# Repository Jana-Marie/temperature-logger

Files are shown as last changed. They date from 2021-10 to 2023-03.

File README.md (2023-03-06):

# temperature-logger

Anotter USB temperature logger that can record up to four channels with thermocouple or NTCs connected via CDC directly or SCPI to USB. You can choose how you want to receive the data by moving the selector switch next to the Type-C receptacle. If you switch to CSV, it will simply output all connected channels to your console in a machine and human readable format (CSV or TSV, I prefer TSV) at about 10 readings per second. If you switch to SCPI, an SCPI terminal is displayed via USB so that you can integrate the logger into your lab equipment. This is particularly handy because you can also use it to control the OC- or H-Bridge outputs, which turns the logger into a thermal IO card. This can be useful when working with Peltier- and heating elements.

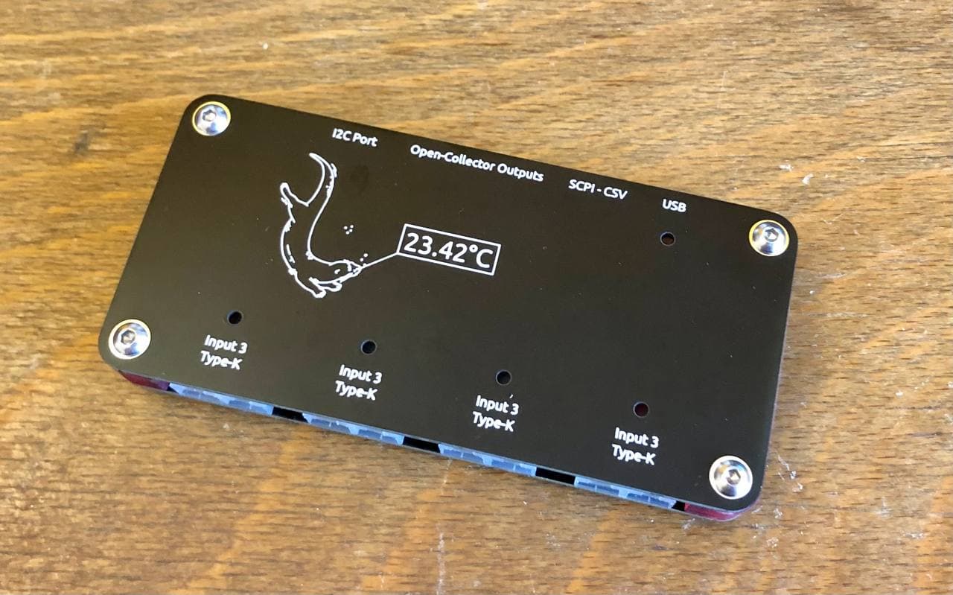
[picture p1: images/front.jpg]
front


Having needed a temperature logger several times in the past, after hacking two together for spontaneous testing, I decided to develop a proper one. This is my result. :3

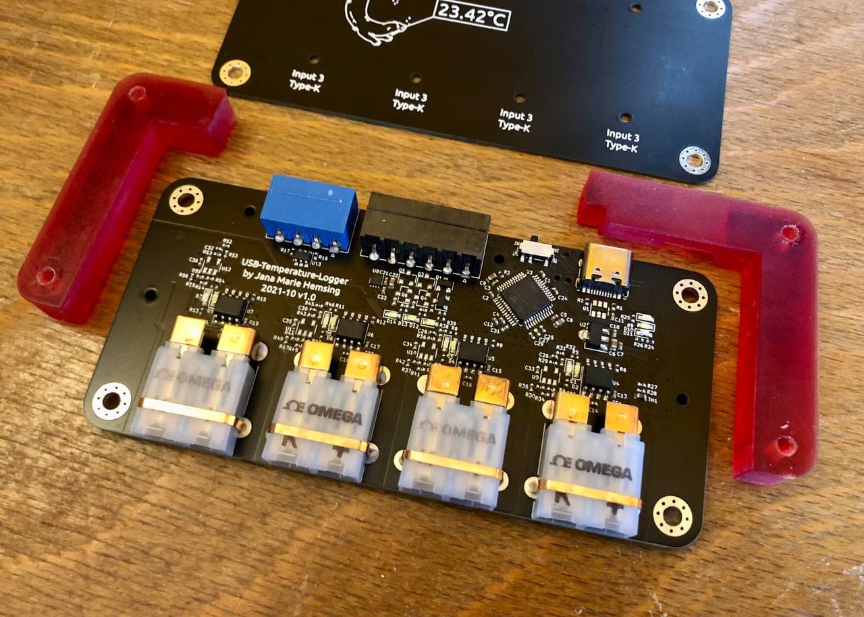
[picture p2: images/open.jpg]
open


### Inputs

Each of the four inputs can either be configured as thermocouple or NTC (resistance measuring) input. At the moment they are assembly options, I need to test if I can assmble both at the same time.

**thermocouple**

One MAX31855KASA can be populated per channel, enabling the reading of K-type thermocouples. Other versions of this IC are available if other thermocouple types are required.

**NTC**

The NTC amplifier is based on [this appnote](https://www.ti.com/lit/an/sboa323a/sboa323a.pdf) and allows amplification of small ranges to the full ADC range. This was an important motivation for this project as I needed a multi-channel body temperature logger.

If you want to know more, you can check out the [schematic](https://github.com/Jana-Marie/temperature-logger/blob/main/temperature-logger.pdf).

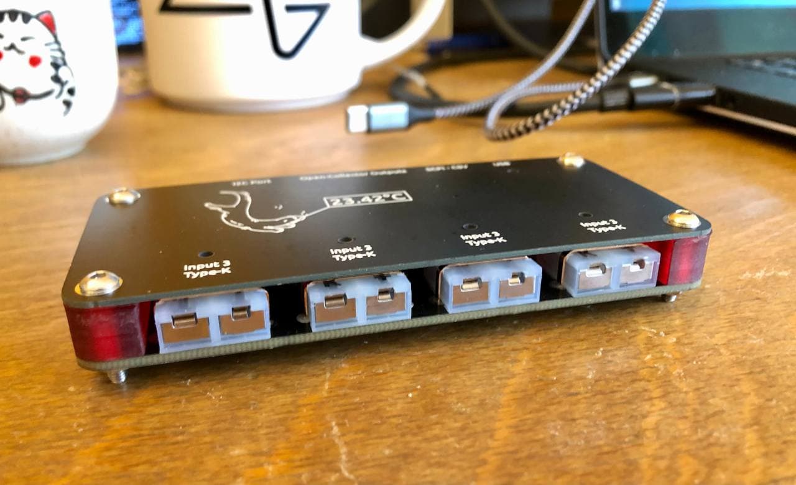
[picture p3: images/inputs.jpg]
inputs


### TODO

 - [ ] implement SCPI - done in the SCPI branch, check it out, but there is not much space left on the STM32, hence no merge yet
 - [ ] add sigrok communication/protocol 

### License

Copyright Jana Marie Hemsing 2023.

This source describes Open Hardware and is licensed under the CERN-OHL-S v2.

You may redistribute and modify this source and make products using it under
the terms of the CERN-OHL-S v2 (https://ohwr.org/cern_ohl_s_v2.txt).

This source is distributed WITHOUT ANY EXPRESS OR IMPLIED WARRANTY,
INCLUDING OF MERCHANTABILITY, SATISFACTORY QUALITY AND FITNESS FOR A
PARTICULAR PURPOSE. Please see the CERN-OHL-S v2 for applicable conditions.

Source location: https://github.com/Jana-Marie/temperature-logger

As per CERN-OHL-S v2 section 4, should You produce hardware based on this
source, You must where practicable maintain the Source Location visible
on the external case of the Gizmo or other products you make using this
source.

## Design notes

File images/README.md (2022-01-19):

front
open
inputs
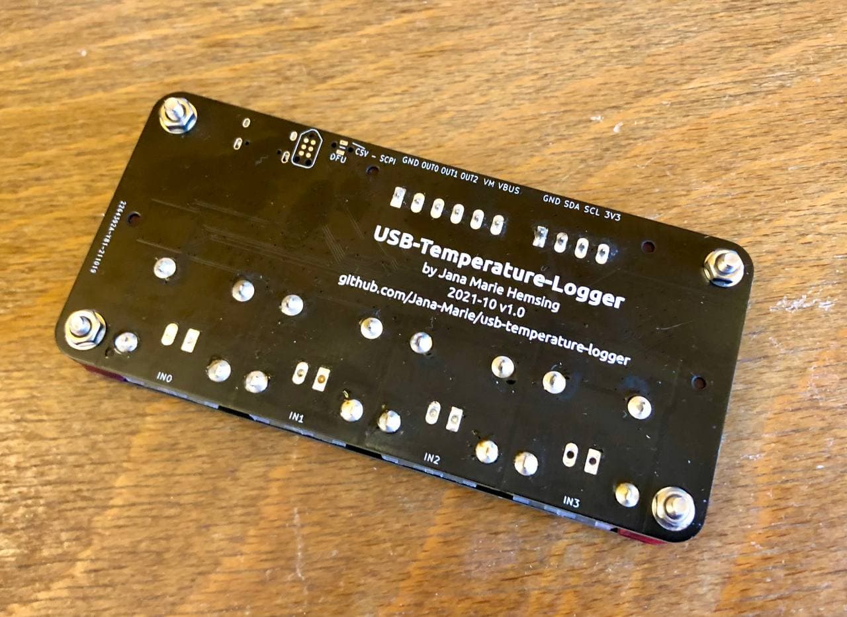
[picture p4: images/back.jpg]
back

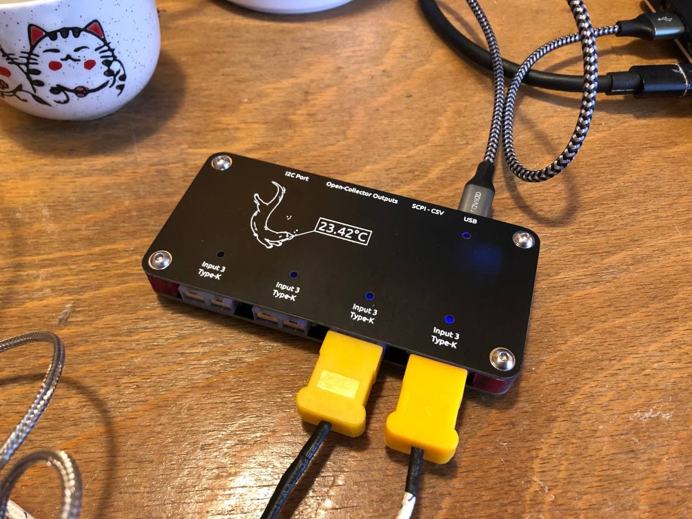
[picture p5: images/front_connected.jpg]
front_connected

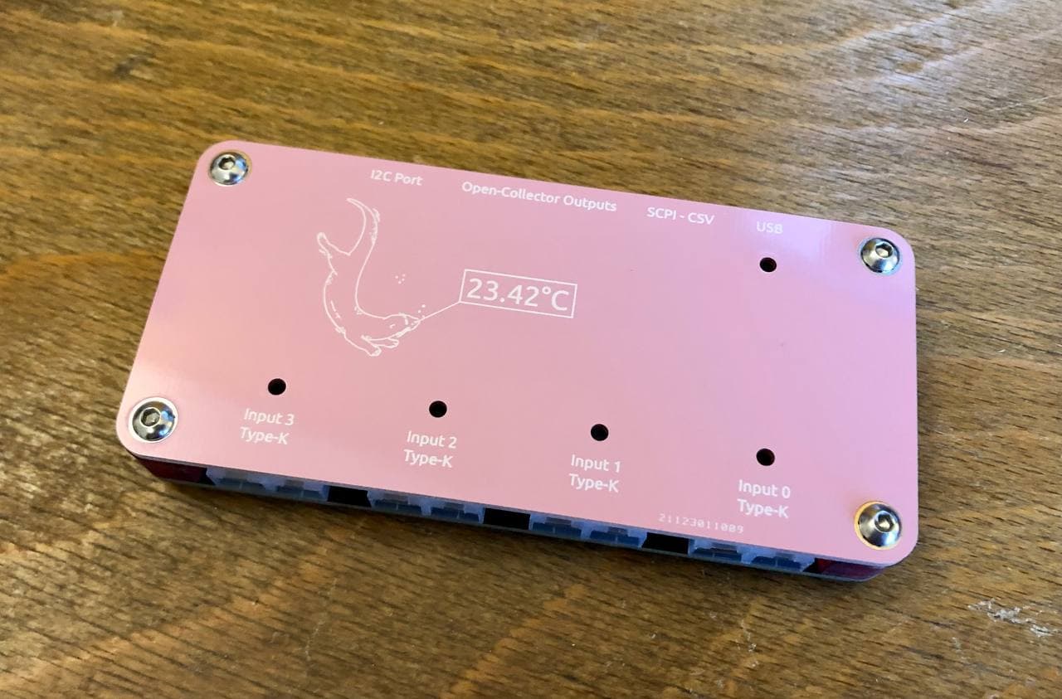
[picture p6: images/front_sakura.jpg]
front_sakura


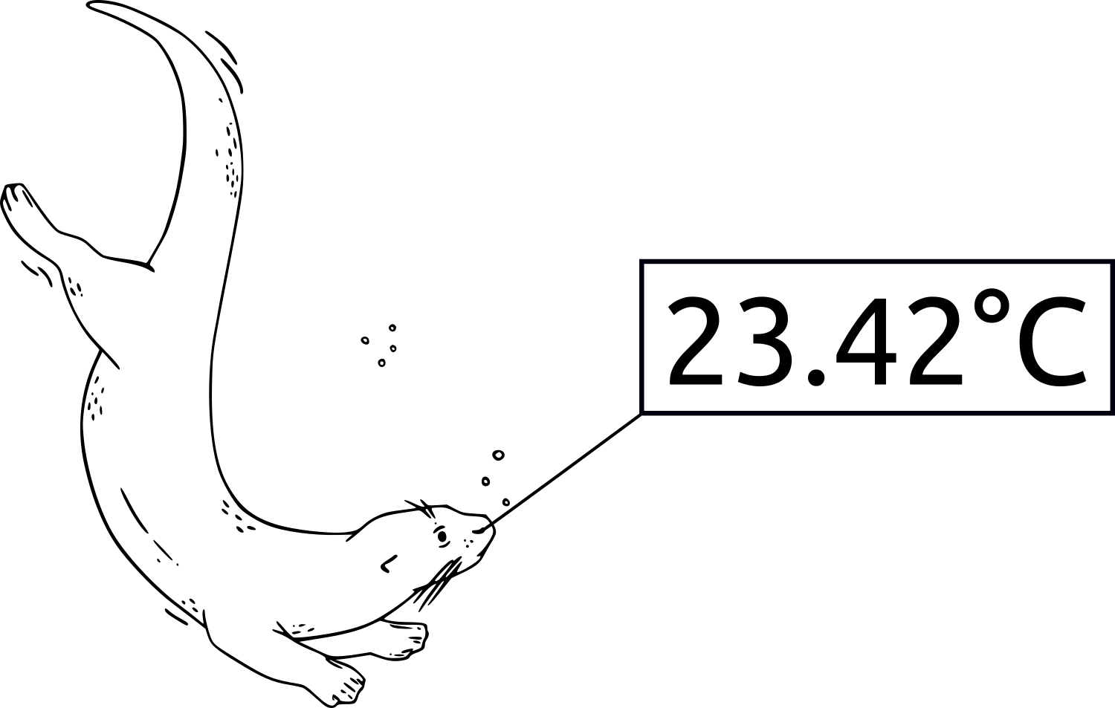
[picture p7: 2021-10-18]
blind_tc/outfiles/text3608.png

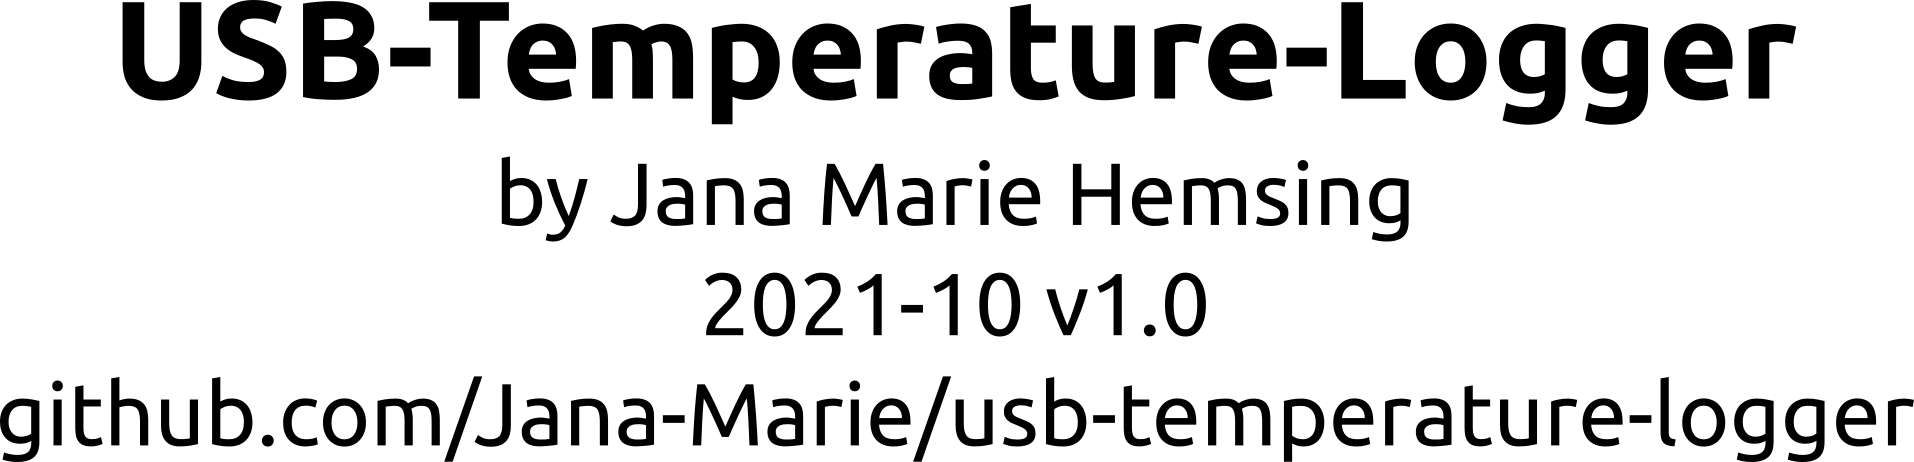
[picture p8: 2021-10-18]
outfiles/text856-3.png

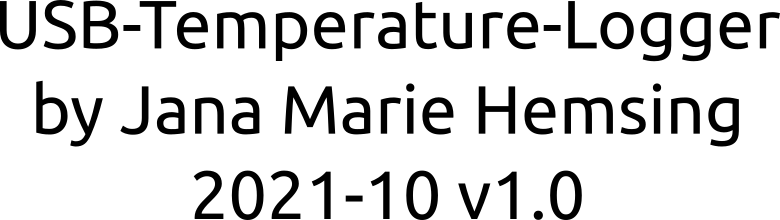
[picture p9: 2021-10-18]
outfiles/text856.png

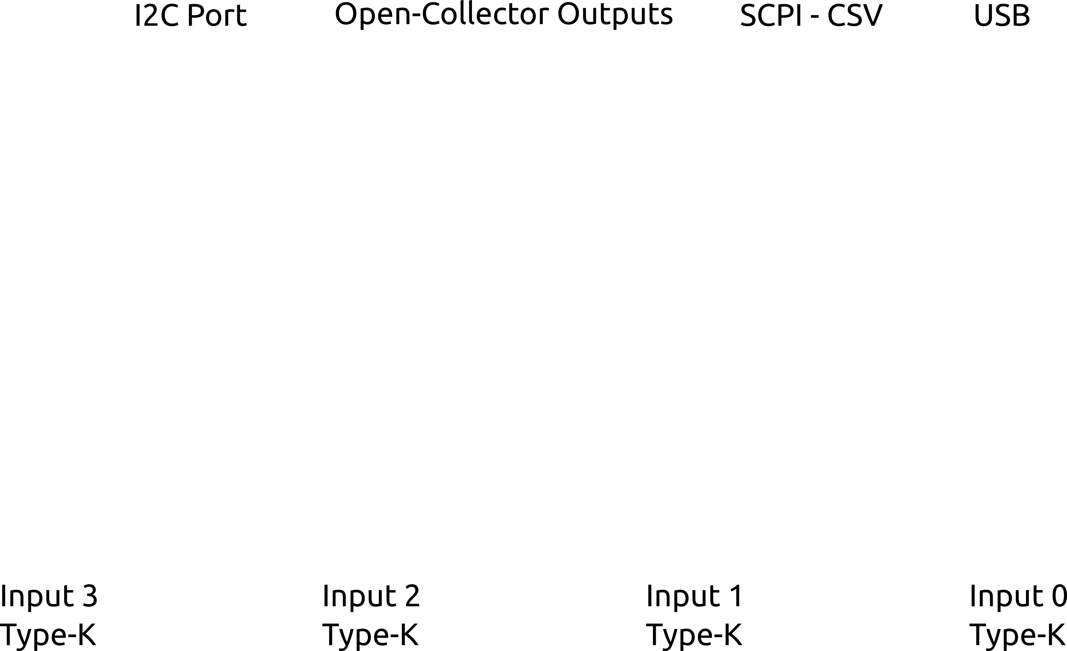
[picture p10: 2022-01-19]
blind_tc/outfiles/text2807.png

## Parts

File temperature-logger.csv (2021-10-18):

Comment | Designator | Footprint | LCSC
100n | C12,C7,C10,C11,C1,C2,C3,C4,C5,C24,C13,C15,C17,C19 | otter:C_0402
10n | C14,C26,C16,C28,C18,C30,C20,C32 | otter:C_0402
DNP | C22 | otter:C_0603
DNP | C25,C33,C27,C34,C29,C35,C31,C36,C23,C21 | otter:C_0402
1uF | C8,C9,C6 | otter:C_0603
GREEN | D10,D2,D4,D6,D8,D14,D13,D12 | otter:LED_0603_1608Metric
BLUE | D11 | otter:LED_0603_1608Metric
RED | D9,D1,D3,D5,D7 | otter:LED_0603_1608Metric
FERRET | FB2,FB1,FB4,FB3,FB6,FB5,FB8,FB7 | otter:L_0402
M3 | H1,H2,H3,H4 | MountingHole:MountingHole_3.2mm_M3_Pad_Via
USB | J1 | otter:USB-C 16Pin
THERMOCOUPLE | J2,J3,J4,J5 | otter:PCC-SMP
OUT | J6 | Connector_Phoenix_MC:PhoenixContact_MC_1,5_6-G-3.5_1x06_P3.50mm_Horizontal
I2C | J7 | Connector_Phoenix_MC:PhoenixContact_MC_1,5_4-G-3.5_1x04_P3.50mm_Horizontal
DNP | J8,J9,J10,J11 | otter:PhoenixContact_MC_1,5_2-G-3.5_1x02_P3.50mm_Horizontal
DFU | JP1 | otter:R_0805
TC2030 | P1 | otter:TC2030
2N7002 | Q1,Q3,Q5 | Package_TO_SOT_SMD:SOT-23
BC817 | Q2,Q4,Q6 | Package_TO_SOT_SMD:SOT-23
5k1 | R1,R2,R3,R27,R28,R16,R17 | otter:R_0402
220 | R24,R25,R26,R4,R5,R7,R8,R10,R11,R13,R14,R19,R18,R21,R20,R23,R22,R59,R58,R57 | otter:R_0402
DNP | R35,R33,R29,R32,R31,R34,R30,R42,R40,R36,R39,R38,R41,R37,R49,R47,R43,R46,R45,R48,R44,R56,R54,R50,R53,R52,R55,R51 | otter:R_0402
10 | R6,R9,R12,R15 | otter:R_0402
SCPI_CSV | SW1 | Button_Switch_SMD:SW_SPDT_PCM12
NTC | TH1 | otter:R_0603
USBLC6-4 | U1,U13 | Package_TO_SOT_SMD:SOT-23-6
AP2204R-3.3 | U2 | Package_TO_SOT_SMD:SOT-89-3
STM32F072C8Tx | U3 | Package_QFP:LQFP-48_7x7mm_P0.5mm
MAX31855KASA | U4,U5,U6,U7 | Package_SO:SOIC-8_3.9x4.9mm_P1.27mm
DRV8837 | U8 | Package_SON:WSON-8-1EP_2x2mm_P0.5mm_EP0.9x1.6mm
TLV9001 | U9,U10,U11,U12 | Package_TO_SOT_SMD:SOT-23-5

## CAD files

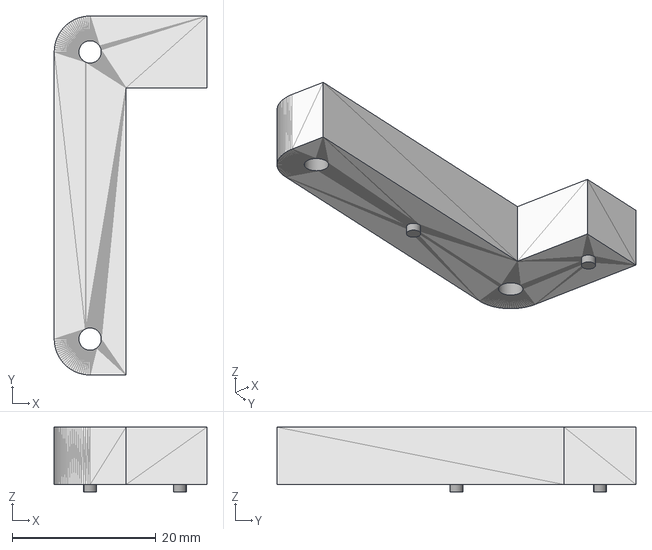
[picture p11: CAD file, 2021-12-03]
3D/spacer_left.step
21.2 x 50.0 x 9.00 mm

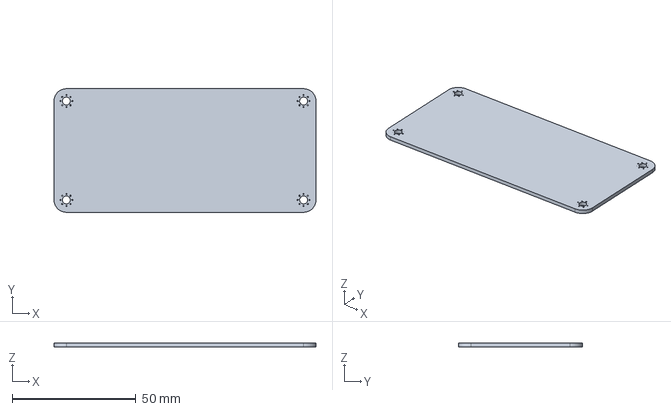
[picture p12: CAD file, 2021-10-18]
blind_tc/blind_tc.step
106.0 x 50.0 x 1.60 mm

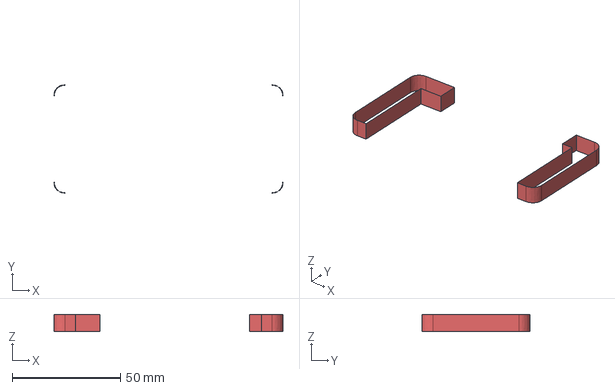
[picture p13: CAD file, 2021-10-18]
outfiles/part.step
106.0 x 50.0 x 8.00 mm

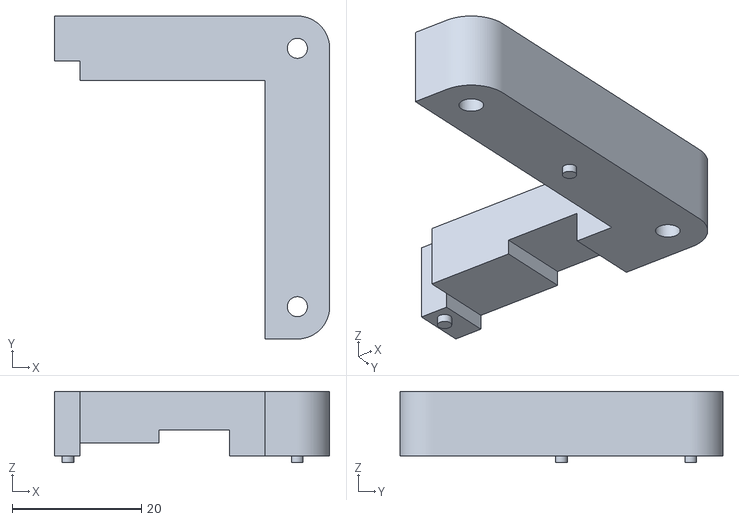
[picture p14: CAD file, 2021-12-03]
3D/sapcer_right.stl
42.6 x 50.0 x 11.0

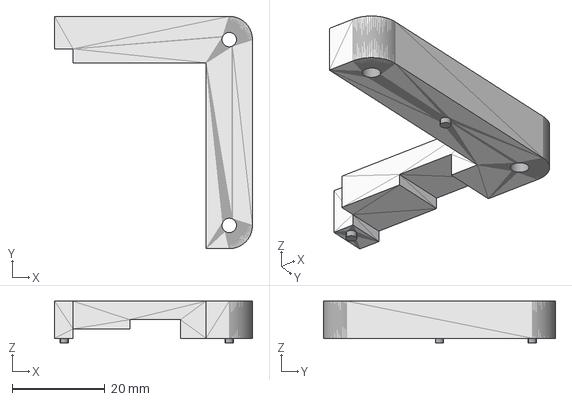
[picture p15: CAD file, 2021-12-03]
3D/spacer_right.step
42.6 x 50.0 x 9.00 mm

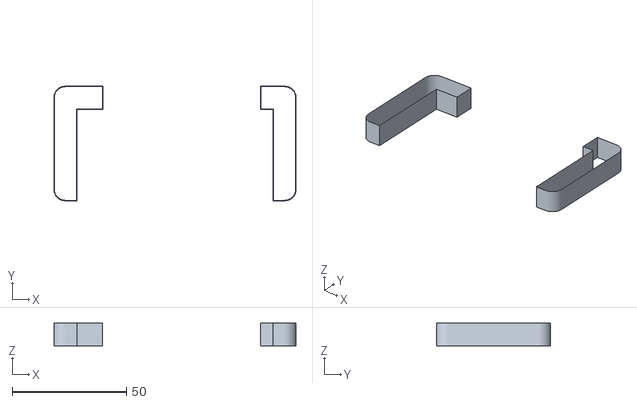
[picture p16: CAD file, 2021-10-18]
outfiles/spacer.stl
106.0 x 50.0 x 10.0

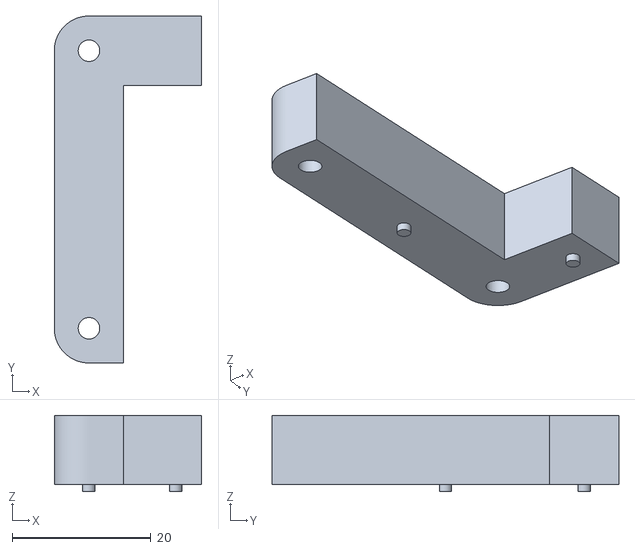
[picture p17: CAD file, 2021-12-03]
3D/sapcer_left.stl
21.2 x 50.0 x 11.0

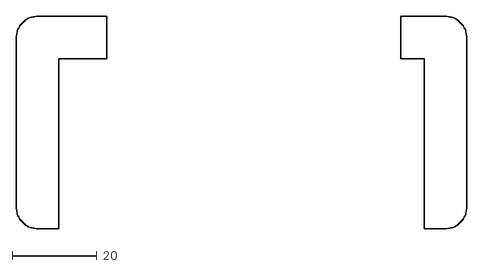
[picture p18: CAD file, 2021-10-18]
outfiles/temperature-logger-brd.dxf
106.0 x 50.0

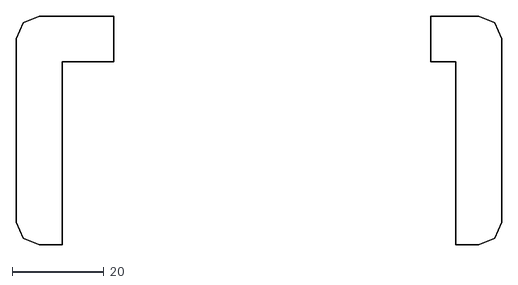
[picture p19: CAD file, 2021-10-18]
outfiles/parts.dxf
106.0 x 50.0

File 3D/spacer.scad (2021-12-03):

$fn = 100;

right();
//left();

module left(z=10){
    difference(){
        union(){
            translate([0,0,z/2])cube([10,40,z],center=true);
            translate([0,20,0])cylinder(r=5,h=z);
            translate([0,-20,0])cylinder(r=5,h=z);
            translate([16.25/2,20,z/2])cube([16.25,10,z],center=true);
            translate([2.5,-20-2.5,z/2])cube([5,5,z],center=true);
            
            translate([0,0,-1])cylinder(r=.9,h=1);
            translate([12.5,20,-1])cylinder(r=.9,h=1);
        } union(){
            translate([0,-20,-0.1])cylinder(d=3.1,h=z+0.2);
            translate([0,20,-0.1])cylinder(d=3.1,h=z+0.2);
        }
    }
}

module right(z=10){
    difference(){
        union(){
            translate([0,0,z/2])cube([10,40,z],center=true);
            translate([-2.5,-20-2.5,z/2])cube([5,5,z],center=true);
            translate([0,20,0])cylinder(r=5,h=z);
            translate([0,-20,0])cylinder(r=5,h=z);
            translate([-10.5/2,20,z/2])cube([10.5,10,z],center=true);
            translate([-10.925/2-10.5,20,z-(z-4)/2])cube([10.925,10,z-4],center=true);
            translate([-12.2/2-10.5-10.925,20,z-(z-2)/2])cube([12.2,10,z-2],center=true);
            translate([-4/2-10.5-10.925-12.2,20+1.5,z/2])cube([4,7,z],center=true);
            
            
            translate([0,0,-1])cylinder(r=.9,h=1);
            translate([-35.5,20,-1])cylinder(r=.9,h=1);
        } union(){
            translate([0,-20,-0.1])cylinder(d=3.1,h=z+0.2);
            translate([0,20,-0.1])cylinder(d=3.1,h=z+0.2);
        }
    }
}

module right_simple(z=8){
    difference(){
        union(){
            translate([0,0,z/2])cube([10,40,z],center=true);
            translate([0,20,0])cylinder(r=5,h=z);
            translate([0,-20,0])cylinder(r=5,h=z);
            translate([-10.5/2,20,z/2])cube([10.5,10,z],center=true);
            //translate([2.5,-20-2.5,z/2])cube([5,5,z],center=true);
            
            translate([0,0,-1])cylinder(r=.9,h=1);
            //translate([12.5,20,-1])cylinder(r=.9,h=1);
        } union(){
            translate([0,-20,-0.1])cylinder(d=3.1,h=z+0.2);
            translate([0,20,-0.1])cylinder(d=3.1,h=z+0.2);
        }
    }
}

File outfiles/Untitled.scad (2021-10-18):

linear_extrude(height = 10, center = true, convexity = 100)
   import (file = "temperature-logger-brd.dxf");

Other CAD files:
outfiles/extrude.step
outfiles/part.FCStd

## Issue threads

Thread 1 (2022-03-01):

### ISSUE TITLE
DRC failures: unconnected GND pin and different pin for NTC_BOARD net

### ISSUE THREAD

**Issue by festlv** [Jana-Marie/temperature-logger#1]
First of all, thanks for sharing this project. I have had a similar need of logging a couple of thermocouple channels, but so far, not enough of a need to design something like this myself.

When reviewing the board before ordering it I noticed a couple of DRC violations- most of them are harmless, but two did catch my attention:
1) Pin 35 of U3 (GND) is not connected- probably a later routing change made it an island.
2) Net NTC_BOARD is connected to pin 29 of U3 in PCB layout, but in schematic it's connected to pin 18.

I'd submit a PR for item #1, but I also squeezed the width of the board a bit to get below 100mm threshold, so that JLCPCB doesn't apply large board engineering fee.

**Comment by Jana-Marie** [comment]
oh, shit, why didn't I get a notification for this issue >.< Will get back to you as soon as possible! The NTC pin is a known issue, I somehow connected it to the wrong pin, fixed it in schematic to not forget it and never updated the board. I will do this as soon as possible!

**Comment by Jana-Marie** [comment]
Also, I would love to see a squeezed version of this board! :O

**Comment by Jana-Marie** [comment]
Please let me know, if you make a squeezed version! :)

**Comment by Jana-Marie** [comment]
omg, this is soo cool! Thank you for sharing it! :)

I think this is super helpful for others, I will order the squeezed version myself for sure. Threaded inserts are awesome, I like that idea. 

May I ask, what do you need/expect from the firmware? It is quite alpha at the moment, I would like to know which part of it would be for your advantage, so I can focus on that?

**Comment by festlv** [comment]
If you're interested, I can ship you my leftover PCBs and stencil, I won't need more boards in forseeable future. I can also print the enclosure and throw in the needed hardware. The only issue is that NTC_BOARD pin needs to be bodged to PB0 (for some reason I went with PA8, without checking that it's not routed to ADC).

Firmware wise I really don't need much- the only thing I noticed was that disconnected TC's are not reported, so the order of channels may change depending on how many channels are connected. For logging purposes I would prefer that channels are always reported in the same order, which would probably imply also reporting disconnected channels.

One thing which I will probably look into myself once I get around it: adding a support for I2C OLED (e.g. SSD1306 based modules) on the expansion port, just to be able to verify that the probes are connected correctly. On the other hand, I guess the LEDs for each channel are also there for this purpose (haha, I now have to check if I haven't soldered them backwards) :)

**Comment by Jana-Marie** [comment]
Okay, perfect, thank you for your input :3

I've pushed a small change, which will always send all channels and show the channel status via the onboard LEDs. Unconnected channels will deliver afaik a very high result, not sure what such a channel should show. Any string might be as annoying as a high number. A typical error-number (-1) would be a valid temperature, I could simply send an empty string there '', not sure if that has any drawbacks. Any suggestions from your side?

The ntc thing is probably my fault, I noticed it, but did not fix it in time. I am sorry for that.

I would be super interested in your boards actually. Do you have an email for me, or should I DM you via twitter?

**Comment by Jana-Marie** [comment]
Whops, had a bug in the FW, the leds do now show the state per channel

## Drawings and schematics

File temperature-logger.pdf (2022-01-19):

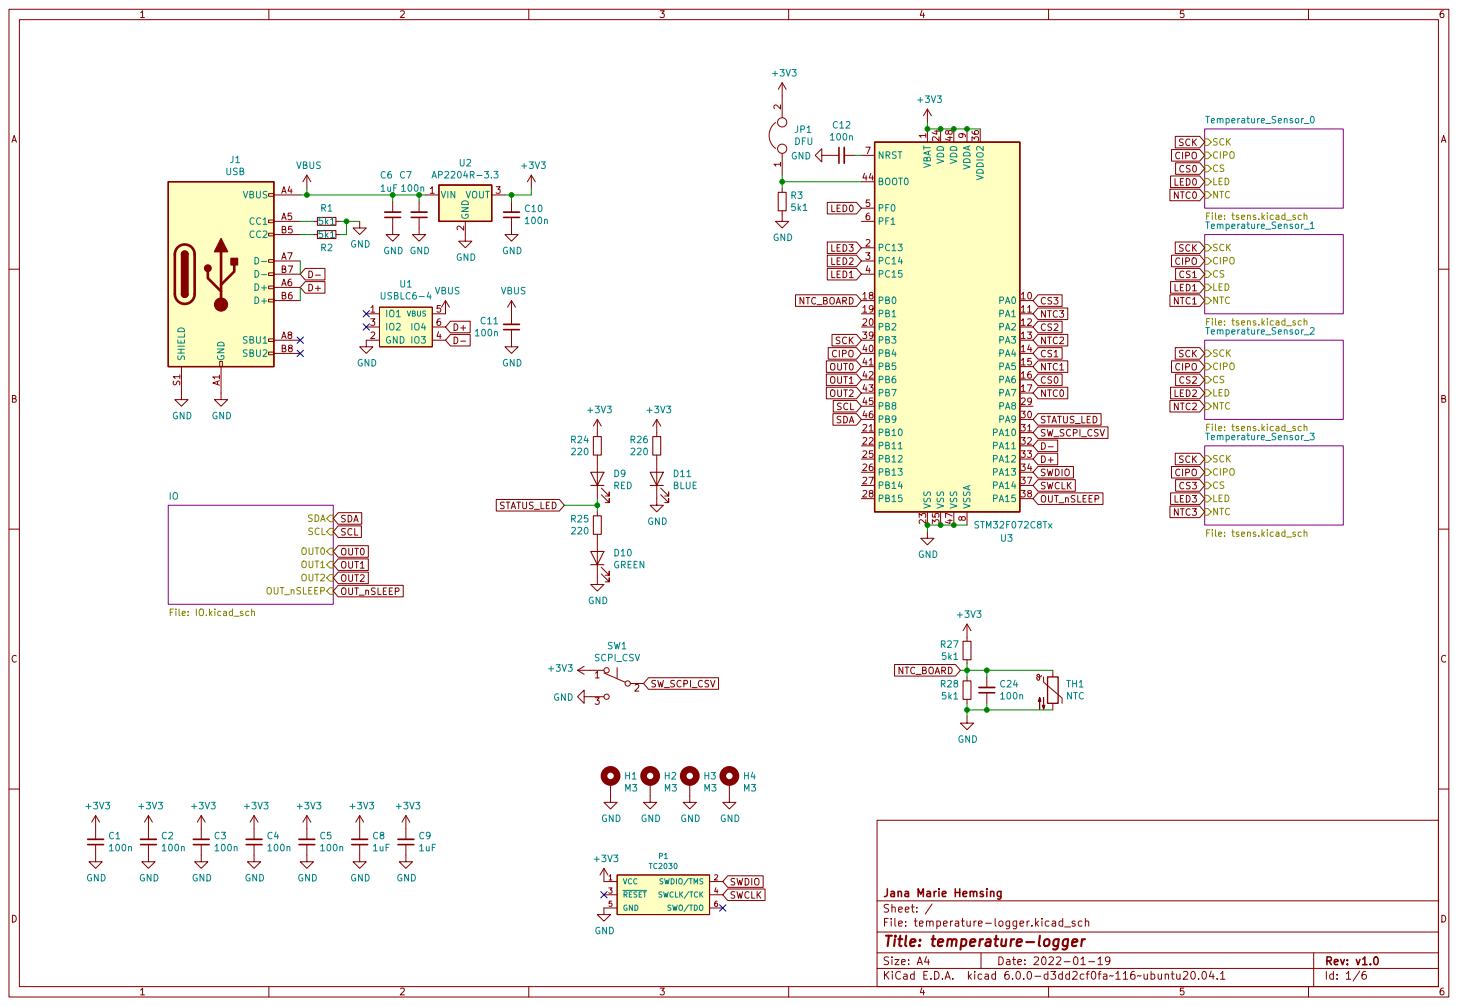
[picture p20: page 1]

1 PA0 10 PA1 11 PA2 12 PA3 13 PA4 14 PA5 15 PA6 16 PA7 17 PB0 18 PB1 19 PC13 2 PB2 20 PB10 21 PB11 22 VSS 23 VDD 24 PB12 25 PB13 26 PB14 27 PB15 28 PA8 29 PC14 3 PA9 30 PA10 31 PA11 32 PA12 33 PA13 34 VSS 35 VDDIO2 36 PA14 37 PA15 38 PB3 39 PC15 4 PB4 40 PB5 41 PB6 42 PB7 43 BOOT0 44 PB8 45 PB9 46 VSS 47 VDD 48 PF0 5 PF1 6 NRST 7 VSSA

File: temperature-logger.kicad_sch Sheet: / Jana Marie Hemsing

Id: 1/6 Title: temperature-logger

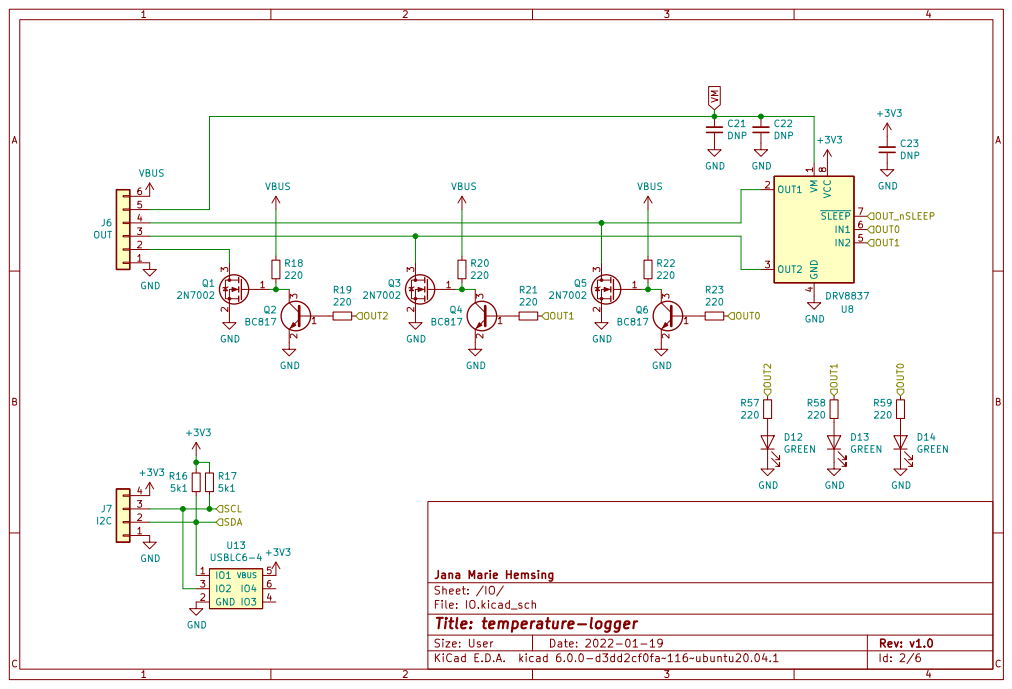
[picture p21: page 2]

Id: 2/6 Title: temperature-logger

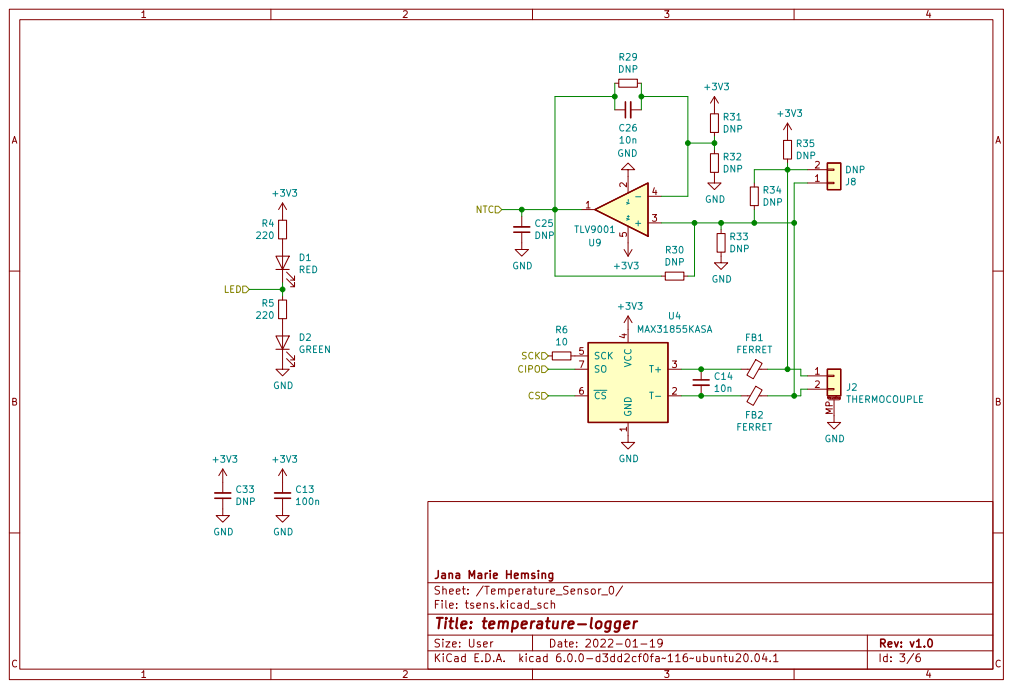
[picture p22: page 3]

Jana Marie Hemsing GND

Sheet: /Temperature_Sensor_0/
File: tsens.kicad_sch
Id: 3/6 Title: temperature-logger

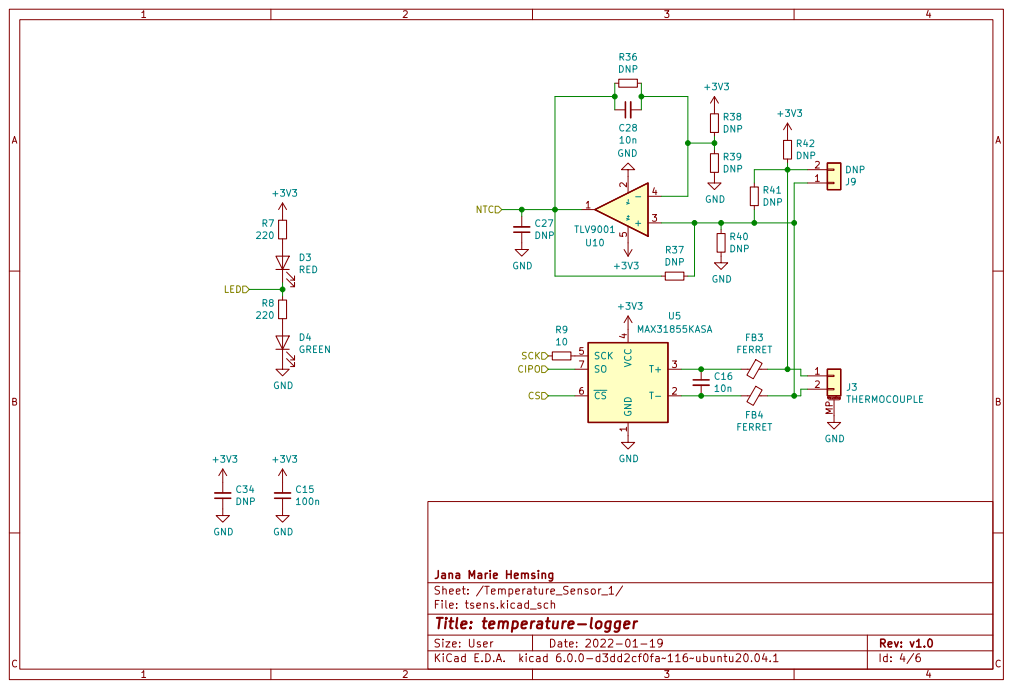
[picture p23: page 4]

Jana Marie Hemsing GND

Sheet: /Temperature_Sensor_1/
File: tsens.kicad_sch
Id: 4/6 Title: temperature-logger

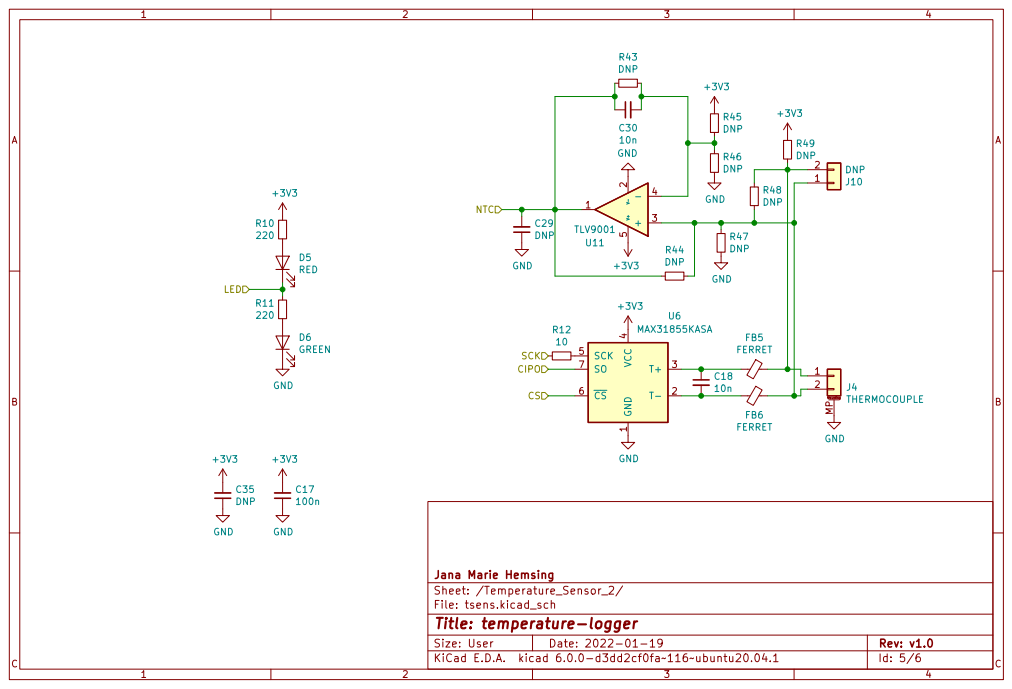
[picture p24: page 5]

Jana Marie Hemsing GND

Sheet: /Temperature_Sensor_2/
File: tsens.kicad_sch
Id: 5/6 Title: temperature-logger

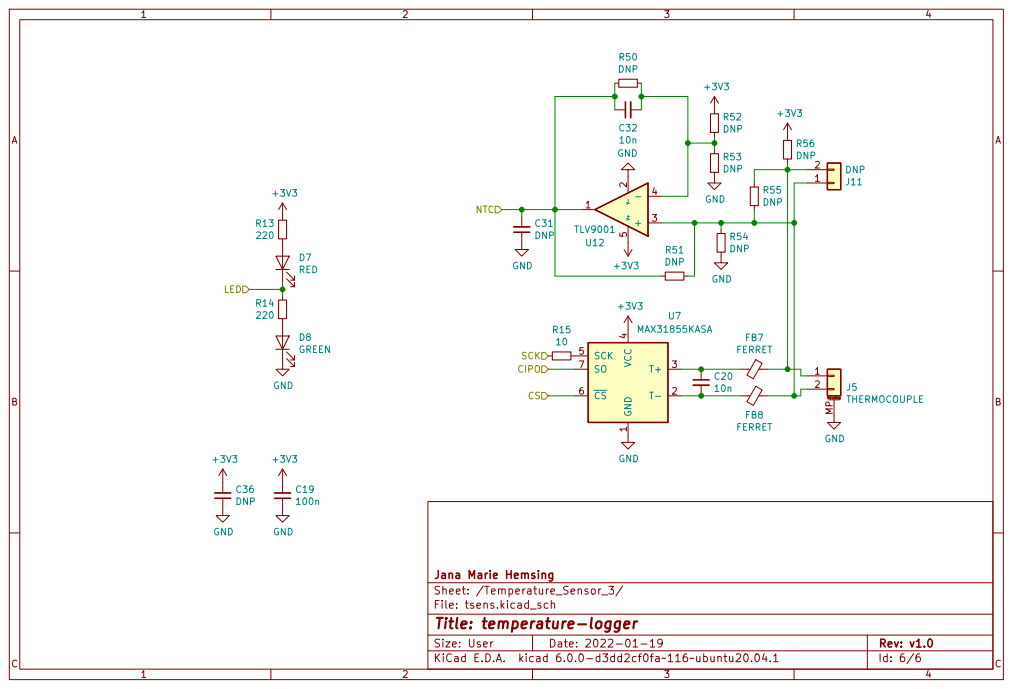
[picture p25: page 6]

Jana Marie Hemsing GND

Sheet: /Temperature_Sensor_3/
File: tsens.kicad_sch
Id: 6/6 Title: temperature-logger

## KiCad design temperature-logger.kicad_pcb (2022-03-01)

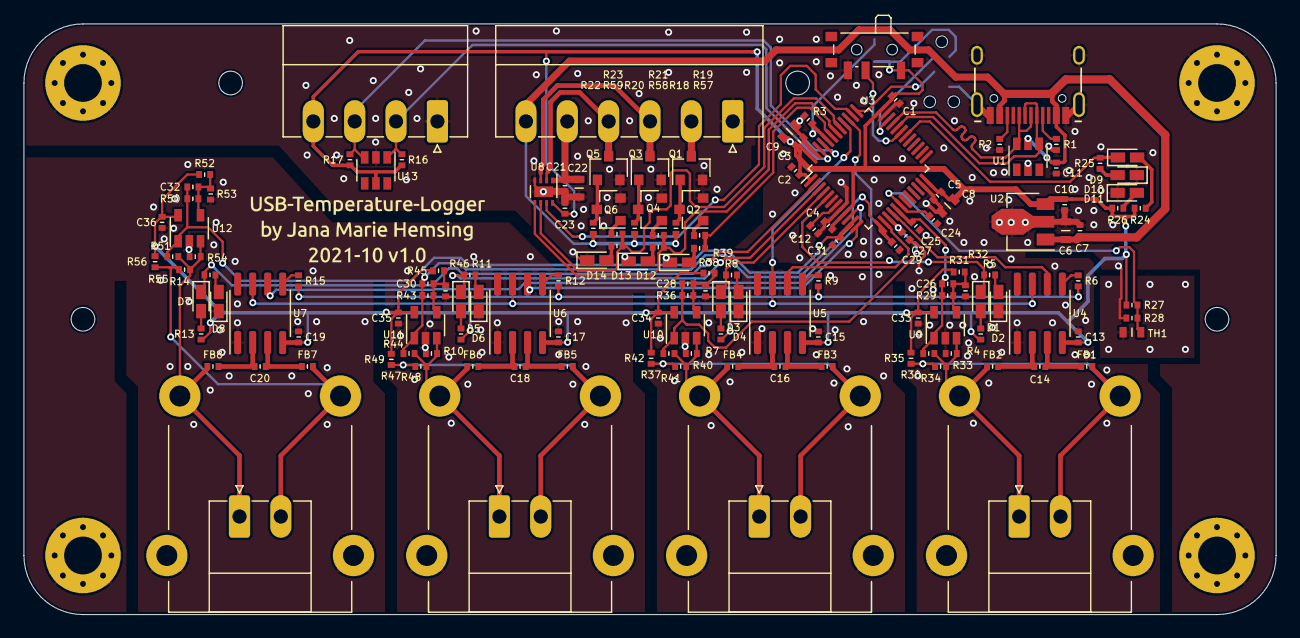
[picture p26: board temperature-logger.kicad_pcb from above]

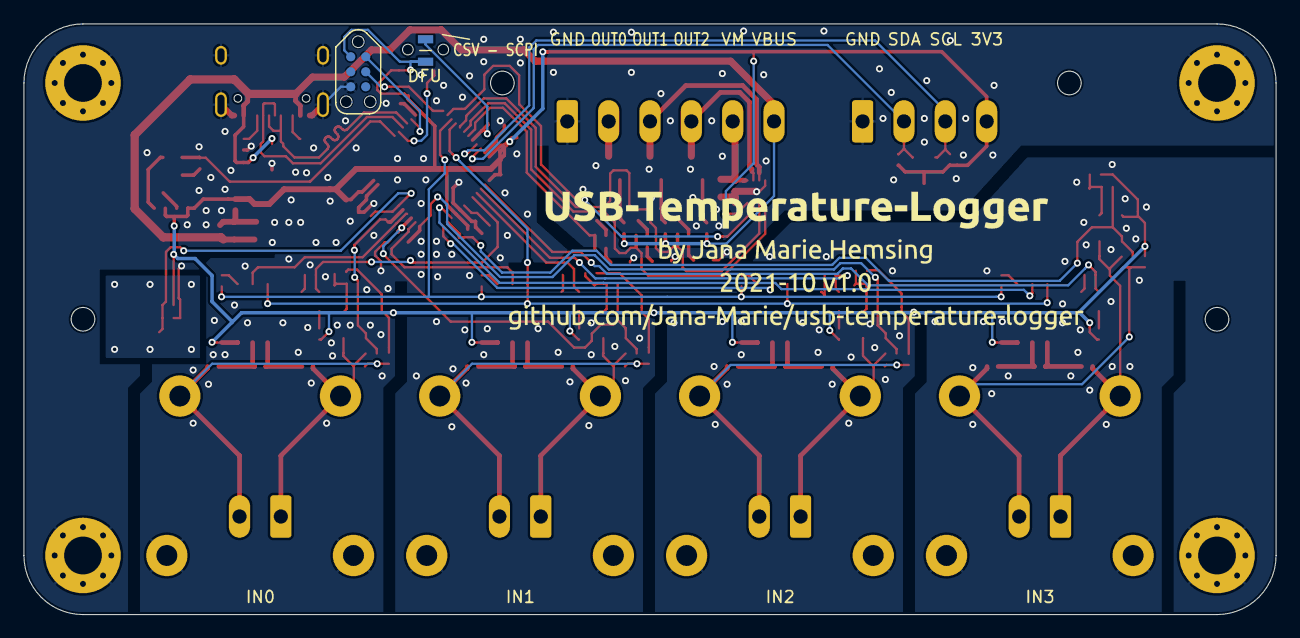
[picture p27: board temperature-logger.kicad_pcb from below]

Board: 4 copper layers, 106.0 x 50.0 mm, 155 parts (2 on the bottom side), 82 nets.

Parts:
C1, C2, C3, C4, C5, C7, C10, C11, C12, C13, C15, C17, C19, C24: 100n; C_0402
C6, C8, C9: 1uF; C_0603
C14, C16, C18, C20, C26, C28, C30, C32: 10n; C_0402
C21, C23, C25, C27, C29, C31, C33, C34, C35, C36: DNP; C_0402
C22: DNP; C_0603
D1, D3, D5, D7, D9: RED; LED_0603_1608Metric
D2, D4, D6, D8, D10, D12, D13, D14: GREEN; LED_0603_1608Metric
D11: BLUE; LED_0603_1608Metric
FB1, FB2, FB3, FB4, FB5, FB6, FB7, FB8: FERRET; L_0402
H1, H2, H3, H4: M3; MountingHole_3.2mm_M3_Pad_Via
J1: USB; USB-C 16Pin
J2, J3, J4, J5: THERMOCOUPLE; PCC-SMP
J6: OUT; PhoenixContact_MC_1,5_6-G-3.5_1x06_P3.50mm_Horizontal
J7: I2C; PhoenixContact_MC_1,5_4-G-3.5_1x04_P3.50mm_Horizontal
J8, J9, J10, J11: DNP; PhoenixContact_MC_1,5_2-G-3.5_1x02_P3.50mm_Horizontal
JP1: DFU; R_0805
P1: TC2030
Q1, Q3, Q5: 2N7002; SOT-23
Q2, Q4, Q6: BC817; SOT-23
R1, R2, R3, R16, R17, R27, R28: 5k1; R_0402
R4, R5, R7, R8, R10, R11, R13, R14, R18, R19, R20, R21, R22, R23, R24, R25, R26, R57, R58, R59: 220; R_0402
R6, R9, R12, R15: 10; R_0402
R29, R30, R31, R32, R33, R34, R35, R36, R37, R38, R39, R40, R41, R42, R43, R44, R45, R46, R47, R48, R49, R50, R51, R52, R53, R54, R55, R56: DNP; R_0402
SW1: SCPI_CSV; SW_SPDT_PCM12
TH1: NTC; R_0603
U1, U13: USBLC6-4; SOT-23-6
U2: AP2204R-3.3; SOT-89-3
U3: STM32F072C8Tx; LQFP-48_7x7mm_P0.5mm
U4, U5, U6, U7: MAX31855KASA; SOIC-8_3.9x4.9mm_P1.27mm
U8: DRV8837; WSON-8-1EP_2x2mm_P0.5mm_EP0.9x1.6mm
U9, U10, U11, U12: TLV9001; SOT-23-5

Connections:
+3V3: C1.2, C2.2, C3.2, C4.2, C5.2, C8.2, C9.2, C10.2, C13.2, C15.2, C17.2, C19.2, C23.2, C33.2, C34.2, C35.2, C36.2, J7.4, JP1.2, P1.1 (VCC), R4.1, R7.1, R10.1, R13.1, R16.1, R17.2, R24.1, R26.1, R27.1, R31.1, R35.1, R38.1, R42.1, R45.1, R49.1, R52.1, R56.1, SW1.1 (A), U2.3 (VOUT), U3.1 (VBAT), U3.9 (VDDA), U3.24 (VDD), U3.36 (VDDIO2), U3.48 (VDD), U4.4 (VCC), U5.4 (VCC), U6.4 (VCC), U7.4 (VCC), U8.8 (VCC), U9.5 (V+), U10.5 (V+), U11.5 (V+), U12.5 (V+), U13.5 (VBUS)
CIPO: U3.40 (PB4), U4.7 (SO), U5.7 (SO), U6.7 (SO), U7.7 (SO)
CS0: U3.16 (PA6), U4.6 (~CS)
CS1: U3.14 (PA4), U5.6 (~CS)
CS2: U3.12 (PA2), U6.6 (~CS)
CS3: U3.10 (PA0), U7.6 (~CS)
D+: J1.A6 (D+), J1.B6 (D+), U1.6 (IO4), U3.33 (PA12)
D-: J1.A7 (D-), J1.B7 (D-), U1.4 (IO3), U3.32 (PA11)
GND: C1.1, C2.1, C3.1, C4.1, C5.1, C6.1, C7.1, C8.1, C9.1, C10.1, C11.1, C12.1, C13.1, C15.1, C17.1, C19.1, C21.1, C22.1, C23.1, C24.1, C25.1, C27.1, C29.1, C31.1, C33.1, C34.1, C35.1, C36.1, D2.1 (K), D4.1 (K), D6.1 (K), D8.1 (K), D10.1 (K), D11.1 (K), D12.1 (K), D13.1 (K), D14.1 (K), H1.1, H2.1, H3.1, H4.1, J1.A1 (GND), J1.A12 (GND), J1.B1 (GND), J1.B12 (GND), J1.S1 (SHIELD), J2.MP (MountPin), J3.MP (MountPin), J4.MP (MountPin), J5.MP (MountPin), J6.1, J7.1, P1.5 (GND), Q1.2 (S), Q2.2 (E), Q3.2 (S), Q4.2 (E), Q5.2 (S), Q6.2 (E), R1.1, R2.2, R3.1, R28.2, R32.2, R33.2, R39.2, R40.2, R46.2, R47.2, R53.2, R54.2, SW1.3 (C), TH1.2, U1.2 (GND), U2.2 (GND), U3.8 (VSSA), U3.23 (VSS), U3.35 (VSS), U3.47 (VSS), U4.1 (GND), U5.1 (GND), U6.1 (GND), U7.1 (GND), U8.4 (GND), U8.9 (GND), U9.2 (V-), U10.2 (V-), U11.2 (V-), U12.2 (V-), U13.2 (GND)
LED0: D1.1 (K), R5.2, U3.5 (PF0)
LED1: D3.1 (K), R8.2, U3.4 (PC15)
LED2: D5.1 (K), R11.2, U3.3 (PC14)
LED3: D7.1 (K), R14.2, U3.2 (PC13)
NTC0: C25.2, C26.1, R29.1, R30.1, U3.17 (PA7), U9.1
NTC1: C27.2, C28.1, R36.1, R37.1, U3.15 (PA5), U10.1
NTC2: C29.2, C30.1, R43.1, R44.1, U3.13 (PA3), U11.1
NTC3: C31.2, C32.1, R50.1, R51.1, U3.11 (PA1), U12.1
NTC_BOARD: C24.2, R27.2, R28.1, TH1.1, U3.18 (PB0)
unnamed: C12.2, U3.7 (NRST)
unnamed: C14.1, FB1.2, U4.3 (T+)
unnamed: C14.2, FB2.2, U4.2 (T-)
unnamed: C16.1, FB3.2, U5.3 (T+)
unnamed: C16.2, FB4.2, U5.2 (T-)
unnamed: C18.1, FB5.2, U6.3 (T+)
unnamed: C18.2, FB6.2, U6.2 (T-)
unnamed: C20.1, FB7.2, U7.3 (T+)
unnamed: C20.2, FB8.2, U7.2 (T-)
unnamed: C26.2, R29.2, R31.2, R32.1, U9.4 (-)
unnamed: C28.2, R36.2, R38.2, R39.1, U10.4 (-)
unnamed: C30.2, R43.2, R45.2, R46.1, U11.4 (-)
unnamed: C32.2, R50.2, R52.2, R53.1, U12.4 (-)
unnamed: D1.2 (A), R4.2
unnamed: D2.2 (A), R5.1
unnamed: D3.2 (A), R7.2
unnamed: D4.2 (A), R8.1
unnamed: D5.2 (A), R10.2
unnamed: D6.2 (A), R11.1
unnamed: D7.2 (A), R13.2
unnamed: D8.2 (A), R14.1
unnamed: D9.2 (A), R24.2
unnamed: D10.2 (A), R25.1
unnamed: D11.2 (A), R26.2
unnamed: D12.2 (A), R57.1
unnamed: D13.2 (A), R58.1
unnamed: D14.2 (A), R59.1
unnamed: FB1.1, J2.1, J8.2, R34.1, R35.2
unnamed: FB2.1, J2.2, J8.1, R30.2, R33.1, R34.2, U9.3 (+)
unnamed: FB3.1, J3.1, J9.2, R41.1, R42.2
unnamed: FB4.1, J3.2, J9.1, R37.2, R40.1, R41.2, U10.3 (+)
unnamed: FB5.1, J4.1, J10.2, R48.1, R49.2
unnamed: FB6.1, J4.2, J10.1, R44.2, R47.1, R48.2, U11.3 (+)
unnamed: FB7.1, J5.1, J11.2, R55.1, R56.2
unnamed: FB8.1, J5.2, J11.1, R51.2, R54.1, R55.2, U12.3 (+)
unnamed: J1.A5 (CC1), R1.2
unnamed: J1.B5 (CC2), R2.1
unnamed: J6.2, Q1.3 (D)
unnamed: J6.3, Q3.3 (D), U8.3 (OUT2)
unnamed: J6.4, Q5.3 (D), U8.2 (OUT1)
unnamed: JP1.1, R3.2, U3.44 (BOOT0)
unnamed: Q1.1 (G), Q2.3 (C), R18.1
unnamed: Q2.1 (B), R19.1
unnamed: Q3.1 (G), Q4.3 (C), R20.1
unnamed: Q4.1 (B), R21.1
unnamed: Q5.1 (G), Q6.3 (C), R22.1
unnamed: Q6.1 (B), R23.1
unnamed: R6.2, U4.5 (SCK)
unnamed: R9.2, U5.5 (SCK)
unnamed: R12.2, U6.5 (SCK)
unnamed: R15.2, U7.5 (SCK)
OUT0: R23.2, R59.2, U3.41 (PB5), U8.6 (IN1)
OUT1: R21.2, R58.2, U3.42 (PB6), U8.5 (IN2)
OUT2: R19.2, R57.2, U3.43 (PB7)
OUT_nSLEEP: U3.38 (PA15), U8.7 (~SLEEP)
SCK: R6.1, R9.1, R12.1, R15.1, U3.39 (PB3)
SCL: J7.3, R17.1, U3.45 (PB8), U13.3 (IO2)
SDA: J7.2, R16.2, U3.46 (PB9), U13.1 (IO1)
STATUS_LED: D9.1 (K), R25.2, U3.30 (PA9)
SWCLK: P1.4 (SWCLK/TCK), U3.37 (PA14)
SWDIO: P1.2 (SWDIO/TMS), U3.34 (PA13)
SW_SCPI_CSV: SW1.2 (B), U3.31 (PA10)
VBUS: C6.2, C7.2, C11.2, J1.A4 (VBUS), J1.A9 (VBUS), J1.B4 (VBUS), J1.B9 (VBUS), J6.6, R18.2, R20.2, R22.2, U1.5 (VBUS), U2.1 (VIN)
VM: C21.2, C22.2, J6.5, U8.1 (VM)

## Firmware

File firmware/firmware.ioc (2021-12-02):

#MicroXplorer Configuration settings - do not modify
ADC.DMAContinuousRequests=ENABLE
ADC.ExternalTrigConv=ADC_EXTERNALTRIGCONV_T2_TRGO
ADC.IPParameters=DMAContinuousRequests,SamplingTime,ExternalTrigConv
ADC.SamplingTime=ADC_SAMPLETIME_55CYCLES_5
Dma.ADC.3.Direction=DMA_PERIPH_TO_MEMORY
Dma.ADC.3.Instance=DMA1_Channel1
Dma.ADC.3.MemDataAlignment=DMA_MDATAALIGN_HALFWORD
Dma.ADC.3.MemInc=DMA_MINC_ENABLE
Dma.ADC.3.Mode=DMA_NORMAL
Dma.ADC.3.PeriphDataAlignment=DMA_PDATAALIGN_HALFWORD
Dma.ADC.3.PeriphInc=DMA_PINC_DISABLE
Dma.ADC.3.Priority=DMA_PRIORITY_LOW
Dma.ADC.3.RequestParameters=Instance,Direction,PeriphInc,MemInc,PeriphDataAlignment,MemDataAlignment,Mode,Priority
Dma.I2C1_RX.1.Direction=DMA_PERIPH_TO_MEMORY
Dma.I2C1_RX.1.Instance=DMA1_Channel7
Dma.I2C1_RX.1.MemDataAlignment=DMA_MDATAALIGN_BYTE
Dma.I2C1_RX.1.MemInc=DMA_MINC_ENABLE
Dma.I2C1_RX.1.Mode=DMA_NORMAL
Dma.I2C1_RX.1.PeriphDataAlignment=DMA_PDATAALIGN_BYTE
Dma.I2C1_RX.1.PeriphInc=DMA_PINC_DISABLE
Dma.I2C1_RX.1.Priority=DMA_PRIORITY_MEDIUM
Dma.I2C1_RX.1.RequestParameters=Instance,Direction,PeriphInc,MemInc,PeriphDataAlignment,MemDataAlignment,Mode,Priority
Dma.I2C1_TX.2.Direction=DMA_MEMORY_TO_PERIPH
Dma.I2C1_TX.2.Instance=DMA1_Channel6
Dma.I2C1_TX.2.MemDataAlignment=DMA_MDATAALIGN_BYTE
Dma.I2C1_TX.2.MemInc=DMA_MINC_ENABLE
Dma.I2C1_TX.2.Mode=DMA_NORMAL
Dma.I2C1_TX.2.PeriphDataAlignment=DMA_PDATAALIGN_BYTE
Dma.I2C1_TX.2.PeriphInc=DMA_PINC_DISABLE
Dma.I2C1_TX.2.Priority=DMA_PRIORITY_MEDIUM
Dma.I2C1_TX.2.RequestParameters=Instance,Direction,PeriphInc,MemInc,PeriphDataAlignment,MemDataAlignment,Mode,Priority
Dma.Request0=SPI1_RX
Dma.Request1=I2C1_RX
Dma.Request2=I2C1_TX
Dma.Request3=ADC
Dma.RequestsNb=4
Dma.SPI1_RX.0.Direction=DMA_PERIPH_TO_MEMORY
Dma.SPI1_RX.0.Instance=DMA1_Channel2
Dma.SPI1_RX.0.MemDataAlignment=DMA_MDATAALIGN_BYTE
Dma.SPI1_RX.0.MemInc=DMA_MINC_ENABLE
Dma.SPI1_RX.0.Mode=DMA_NORMAL
Dma.SPI1_RX.0.PeriphDataAlignment=DMA_PDATAALIGN_BYTE
Dma.SPI1_RX.0.PeriphInc=DMA_PINC_DISABLE
Dma.SPI1_RX.0.Priority=DMA_PRIORITY_HIGH
Dma.SPI1_RX.0.RequestParameters=Instance,Direction,PeriphInc,MemInc,PeriphDataAlignment,MemDataAlignment,Mode,Priority
File.Version=6
GPIO.groupedBy=
I2C1.I2C_Speed_Mode=I2C_Fast
I2C1.IPParameters=I2C_Speed_Mode,Timing,OwnAddress
I2C1.OwnAddress=42
I2C1.Timing=0x0000020B
KeepUserPlacement=false
Mcu.Family=STM32F0
Mcu.IP0=ADC
Mcu.IP1=DMA
Mcu.IP2=I2C1
Mcu.IP3=NVIC
Mcu.IP4=RCC
Mcu.IP5=SPI1
Mcu.IP6=SYS
Mcu.IP7=TIM1
Mcu.IP8=TIM2
Mcu.IP9=USB
Mcu.IPNb=10
Mcu.Name=STM32F072C(8-B)Tx
Mcu.Package=LQFP48
Mcu.Pin0=PC13
Mcu.Pin1=PC14-OSC32_IN
Mcu.Pin10=PA6
Mcu.Pin11=PA7
Mcu.Pin12=PB0
Mcu.Pin13=PA9
Mcu.Pin14=PA10
Mcu.Pin15=PA11
Mcu.Pin16=PA12
Mcu.Pin17=PA13
Mcu.Pin18=PA14
Mcu.Pin19=PA15
Mcu.Pin2=PC15-OSC32_OUT
Mcu.Pin20=PB3
Mcu.Pin21=PB4
Mcu.Pin22=PB5
Mcu.Pin23=PB6
Mcu.Pin24=PB7
Mcu.Pin25=PB8
Mcu.Pin26=PB9
Mcu.Pin27=VP_ADC_TempSens_Input
Mcu.Pin28=VP_SYS_VS_Systick
Mcu.Pin29=VP_TIM1_VS_ClockSourceINT
Mcu.Pin3=PF0-OSC_IN
Mcu.Pin30=VP_TIM1_VS_no_output1
Mcu.Pin31=VP_TIM2_VS_ClockSourceINT
Mcu.Pin4=PA0
Mcu.Pin5=PA1
Mcu.Pin6=PA2
Mcu.Pin7=PA3
Mcu.Pin8=PA4
Mcu.Pin9=PA5
Mcu.PinsNb=32
Mcu.ThirdPartyNb=0
Mcu.UserConstants=
Mcu.UserName=STM32F072C8Tx
MxCube.Version=6.3.0
MxDb.Version=DB.6.0.30
NVIC.DMA1_Channel1_IRQn=true\:0\:0\:false\:false\:true\:false\:true
NVIC.DMA1_Channel2_3_IRQn=true\:0\:0\:false\:false\:true\:false\:true
NVIC.DMA1_Channel4_5_6_7_IRQn=true\:0\:0\:false\:false\:true\:false\:true
NVIC.ForceEnableDMAVector=true
NVIC.HardFault_IRQn=true\:0\:0\:false\:false\:true\:false\:false
NVIC.NonMaskableInt_IRQn=true\:0\:0\:false\:false\:true\:false\:false
NVIC.PendSV_IRQn=true\:0\:0\:false\:false\:true\:false\:false
NVIC.SVC_IRQn=true\:0\:0\:false\:false\:true\:false\:false
NVIC.SysTick_IRQn=true\:3\:0\:false\:false\:true\:false\:true
NVIC.TIM1_BRK_UP_TRG_COM_IRQn=true\:0\:0\:false\:false\:true\:true\:true
NVIC.TIM1_CC_IRQn=true\:0\:0\:false\:false\:true\:true\:true
NVIC.TIM2_IRQn=true\:0\:0\:false\:false\:true\:true\:true
PA0.GPIOParameters=GPIO_Label
PA0.GPIO_Label=NSS3
PA0.Locked=true
PA0.Signal=GPIO_Output
PA1.GPIOParameters=GPIO_Label
PA1.GPIO_Label=NTC3
PA1.Mode=IN1
PA1.Signal=ADC_IN1
PA10.GPIOParameters=GPIO_Label
PA10.GPIO_Label=SW_SCPI_CSV
PA10.Locked=true
PA10.Signal=GPIO_Input
PA11.Locked=true
PA11.Mode=Device
PA11.Signal=USB_DM
PA12.Mode=Device
PA12.Signal=USB_DP
PA13.Locked=true
PA13.Mode=Serial_Wire
PA13.Signal=SYS_SWDIO
PA14.Mode=Serial_Wire
PA14.Signal=SYS_SWCLK
PA15.GPIOParameters=GPIO_Label
PA15.GPIO_Label=OUT_nSLEEP
PA15.Locked=true
PA15.Signal=GPIO_Output
PA2.GPIOParameters=GPIO_Label
PA2.GPIO_Label=NSS2
PA2.Locked=true
PA2.Signal=GPIO_Output
PA3.GPIOParameters=GPIO_Label
PA3.GPIO_Label=NTC2
PA3.Mode=IN3
PA3.Signal=ADC_IN3
PA4.GPIOParameters=GPIO_Label
PA4.GPIO_Label=NSS1
PA4.Locked=true
PA4.Signal=GPIO_Output
PA5.GPIOParameters=GPIO_Label
PA5.GPIO_Label=NTC1
PA5.Mode=IN5
PA5.Signal=ADC_IN5
PA6.GPIOParameters=GPIO_Label
PA6.GPIO_Label=NSS0
PA6.Locked=true
PA6.Signal=GPIO_Output
PA7.GPIOParameters=GPIO_Label
PA7.GPIO_Label=NTC0
PA7.Mode=IN7
PA7.Signal=ADC_IN7
PA9.GPIOParameters=GPIO_Label
PA9.GPIO_Label=LED_STATUS
PA9.Locked=true
PA9.Signal=GPIO_Output
PB0.GPIOParameters=GPIO_Label
PB0.GPIO_Label=NTC_BOARD
PB0.Mode=IN8
PB0.Signal=ADC_IN8
PB3.Locked=true
PB3.Mode=RX_Only_Simplex_Unidirect_Master
PB3.Signal=SPI1_SCK
PB4.Locked=true
PB4.Mode=RX_Only_Simplex_Unidirect_Master
PB4.Signal=SPI1_MISO
PB5.GPIOParameters=GPIO_Label
PB5.GPIO_Label=OUT0
PB5.Locked=true
PB5.Signal=GPIO_Output
PB6.GPIOParameters=GPIO_Label
PB6.GPIO_Label=OUT1
PB6.Locked=true
PB6.Signal=GPIO_Output
PB7.GPIOParameters=GPIO_Label
PB7.GPIO_Label=OUT2
PB7.Locked=true
PB7.Signal=GPIO_Output
PB8.Locked=true
PB8.Mode=I2C
PB8.Signal=I2C1_SCL
PB9.Locked=true
PB9.Mode=I2C
PB9.Signal=I2C1_SDA
PC13.GPIOParameters=GPIO_Label
PC13.GPIO_Label=LED3
PC13.Locked=true
PC13.Signal=GPIO_Output
PC14-OSC32_IN.GPIOParameters=GPIO_Label
PC14-OSC32_IN.GPIO_Label=LED2
PC14-OSC32_IN.Locked=true
PC14-OSC32_IN.Signal=GPIO_Output
PC15-OSC32_OUT.GPIOParameters=GPIO_Label
PC15-OSC32_OUT.GPIO_Label=LED1
PC15-OSC32_OUT.Locked=true
PC15-OSC32_OUT.Signal=GPIO_Output
PF0-OSC_IN.GPIOParameters=GPIO_Label
PF0-OSC_IN.GPIO_Label=LED0
PF0-OSC_IN.Locked=true
PF0-OSC_IN.Signal=GPIO_Output
PinOutPanel.RotationAngle=0
ProjectManager.AskForMigrate=true
ProjectManager.BackupPrevious=false
ProjectManager.CompilerOptimize=6
ProjectManager.ComputerToolchain=false
ProjectManager.CoupleFile=false
ProjectManager.CustomerFirmwarePackage=
ProjectManager.DefaultFWLocation=true
ProjectManager.DeletePrevious=true
ProjectManager.DeviceId=STM32F072C8Tx
ProjectManager.FirmwarePackage=STM32Cube FW_F0 V1.11.3
ProjectManager.FreePins=false
ProjectManager.HalAssertFull=false
ProjectManager.HeapSize=0x200
ProjectManager.KeepUserCode=true
ProjectManager.LastFirmware=true
ProjectManager.LibraryCopy=1
ProjectManager.MainLocation=Core/Src
ProjectManager.NoMain=false
ProjectManager.PreviousToolchain=
ProjectManager.ProjectBuild=false
ProjectManager.ProjectFileName=firmware.ioc
ProjectManager.ProjectName=firmware
ProjectManager.RegisterCallBack=
ProjectManager.StackSize=0x400
ProjectManager.TargetToolchain=Makefile
ProjectManager.ToolChainLocation=
ProjectManager.UnderRoot=false
ProjectManager.functionlistsort=1-MX_GPIO_Init-GPIO-false-HAL-true,2-MX_DMA_Init-DMA-false-HAL-true,3-SystemClock_Config-RCC-false-HAL-false,4-MX_SPI1_Init-SPI1-false-HAL-true,5-MX_USB_PCD_Init-USB-false-HAL-true,6-MX_I2C1_Init-I2C1-false-HAL-true,7-MX_TIM1_Init-TIM1-false-HAL-true,8-MX_ADC_Init-ADC-false-HAL-true,9-MX_TIM2_Init-TIM2-false-HAL-true
RCC.AHBFreq_Value=48000000
RCC.APB1Freq_Value=48000000
RCC.APB1TimFreq_Value=48000000
RCC.CECFreq_Value=32786.88524590164
RCC.FCLKCortexFreq_Value=48000000
RCC.FamilyName=M
RCC.HCLKFreq_Value=48000000
RCC.HSICECFreq_Value=32786.88524590164
RCC.I2SFreq_Value=48000000
RCC.IPParameters=AHBFreq_Value,APB1Freq_Value,APB1TimFreq_Value,CECFreq_Value,FCLKCortexFreq_Value,FamilyName,HCLKFreq_Value,HSICECFreq_Value,I2SFreq_Value,MCOFreq_Value,PLLCLKFreq_Value,PLLMCOFreq_Value,SYSCLKFreq_VALUE,SYSCLKSource,TimSysFreq_Value,USART1Freq_Value,USART2Freq_Value,VCOOutput2Freq_Value
RCC.MCOFreq_Value=48000000
RCC.PLLCLKFreq_Value=16000000
RCC.PLLMCOFreq_Value=16000000
RCC.SYSCLKFreq_VALUE=48000000
RCC.SYSCLKSource=RCC_SYSCLKSOURCE_HSI48
RCC.TimSysFreq_Value=48000000
RCC.USART1Freq_Value=48000000
RCC.USART2Freq_Value=48000000
RCC.VCOOutput2Freq_Value=8000000
SPI1.BaudRatePrescaler=SPI_BAUDRATEPRESCALER_16
SPI1.CalculateBaudRate=3.0 MBits/s
SPI1.DataSize=SPI_DATASIZE_8BIT
SPI1.Direction=SPI_DIRECTION_2LINES_RXONLY
SPI1.IPParameters=VirtualType,Mode,Direction,CalculateBaudRate,DataSize,BaudRatePrescaler
SPI1.Mode=SPI_MODE_MASTER
SPI1.VirtualType=VM_MASTER
TIM1.AutoReloadPreload=TIM_AUTORELOAD_PRELOAD_ENABLE
TIM1.Channel-Output\ Compare1\ No\ Output=TIM_CHANNEL_1
TIM1.IPParameters=Channel-Output Compare1 No Output,AutoReloadPreload,Pulse-Output Compare1 No Output,Prescaler,Period
TIM1.Period=1024
TIM1.Prescaler=16
TIM1.Pulse-Output\ Compare1\ No\ Output=100
TIM2.AutoReloadPreload=TIM_AUTORELOAD_PRELOAD_ENABLE
TIM2.IPParameters=Period,AutoReloadPreload,Prescaler
TIM2.Period=1024
TIM2.Prescaler=16
VP_ADC_TempSens_Input.Mode=IN-TempSens
VP_ADC_TempSens_Input.Signal=ADC_TempSens_Input
VP_SYS_VS_Systick.Mode=SysTick
VP_SYS_VS_Systick.Signal=SYS_VS_Systick
VP_TIM1_VS_ClockSourceINT.Mode=Internal
VP_TIM1_VS_ClockSourceINT.Signal=TIM1_VS_ClockSourceINT
VP_TIM1_VS_no_output1.Mode=Output Compare1 No Output
VP_TIM1_VS_no_output1.Signal=TIM1_VS_no_output1
VP_TIM2_VS_ClockSourceINT.Mode=Internal
VP_TIM2_VS_ClockSourceINT.Signal=TIM2_VS_ClockSourceINT
board=custom

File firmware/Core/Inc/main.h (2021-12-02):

/* USER CODE BEGIN Header */
/**
  ******************************************************************************
  * @file           : main.h
  * @brief          : Header for main.c file.
  *                   This file contains the common defines of the application.
  ******************************************************************************
  * @attention
  *
  * <h2><center>&copy; Copyright (c) 2021 STMicroelectronics.
  * All rights reserved.</center></h2>
  *
  * This software component is licensed by ST under BSD 3-Clause license,
  * the "License"; You may not use this file except in compliance with the
  * License. You may obtain a copy of the License at:
  *                        opensource.org/licenses/BSD-3-Clause
  *
  ******************************************************************************
  */
/* USER CODE END Header */

/* Define to prevent recursive inclusion -------------------------------------*/
#ifndef __MAIN_H
#define __MAIN_H

#ifdef __cplusplus
extern "C" {
#endif

/* Includes ------------------------------------------------------------------*/
#include "stm32f0xx_hal.h"

/* Private includes ----------------------------------------------------------*/
/* USER CODE BEGIN Includes */

/* USER CODE END Includes */

/* Exported types ------------------------------------------------------------*/
/* USER CODE BEGIN ET */

/* USER CODE END ET */

/* Exported constants --------------------------------------------------------*/
/* USER CODE BEGIN EC */

/* USER CODE END EC */

/* Exported macro ------------------------------------------------------------*/
/* USER CODE BEGIN EM */

/* USER CODE END EM */

/* Exported functions prototypes ---------------------------------------------*/
void Error_Handler(void);

/* USER CODE BEGIN EFP */

/* USER CODE END EFP */

/* Private defines -----------------------------------------------------------*/
#define LED3_Pin GPIO_PIN_13
#define LED3_GPIO_Port GPIOC
#define LED2_Pin GPIO_PIN_14
#define LED2_GPIO_Port GPIOC
#define LED1_Pin GPIO_PIN_15
#define LED1_GPIO_Port GPIOC
#define LED0_Pin GPIO_PIN_0
#define LED0_GPIO_Port GPIOF
#define NSS3_Pin GPIO_PIN_0
#define NSS3_GPIO_Port GPIOA
#define NTC3_Pin GPIO_PIN_1
#define NTC3_GPIO_Port GPIOA
#define NSS2_Pin GPIO_PIN_2
#define NSS2_GPIO_Port GPIOA
#define NTC2_Pin GPIO_PIN_3
#define NTC2_GPIO_Port GPIOA
#define NSS1_Pin GPIO_PIN_4
#define NSS1_GPIO_Port GPIOA
#define NTC1_Pin GPIO_PIN_5
#define NTC1_GPIO_Port GPIOA
#define NSS0_Pin GPIO_PIN_6
#define NSS0_GPIO_Port GPIOA
#define NTC0_Pin GPIO_PIN_7
#define NTC0_GPIO_Port GPIOA
#define NTC_BOARD_Pin GPIO_PIN_0
#define NTC_BOARD_GPIO_Port GPIOB
#define LED_STATUS_Pin GPIO_PIN_9
#define LED_STATUS_GPIO_Port GPIOA
#define SW_SCPI_CSV_Pin GPIO_PIN_10
#define SW_SCPI_CSV_GPIO_Port GPIOA
#define OUT_nSLEEP_Pin GPIO_PIN_15
#define OUT_nSLEEP_GPIO_Port GPIOA
#define OUT0_Pin GPIO_PIN_5
#define OUT0_GPIO_Port GPIOB
#define OUT1_Pin GPIO_PIN_6
#define OUT1_GPIO_Port GPIOB
#define OUT2_Pin GPIO_PIN_7
#define OUT2_GPIO_Port GPIOB
/* USER CODE BEGIN Private defines */

/* USER CODE END Private defines */

#ifdef __cplusplus
}
#endif

#endif /* __MAIN_H */

/************************ (C) COPYRIGHT STMicroelectronics *****END OF FILE****/

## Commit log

2021-10-18 exported gerbers
    [IO.sch, blind_tc-B_Cu.gbl, blind_tc-B_Mask.gbs, blind_tc-B_Paste.gbp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]
2021-12-03 added HW files
    [temperature-logger.kicad_pcb, temperature-logger.sch]
2021-12-03 added 3d files
    [sapcer_left.stl, sapcer_right.stl, spacer.scad, spacer_left.step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]
2022-01-19 updated to kicad 6
    [temperature-logger.kicad_pcb, temperature-logger.kicad_sch]
2022-01-19 updated blind to kicad 6
    [blind_tc-B_Cu.gbl, blind_tc-B_Mask.gbs, blind_tc-B_Paste.gbp, blind_tc-B_SilkS.gbo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]
2022-03-01 fixed isses #1
    [temperature-logger.kicad_pcb]
2022-03-01 udated gerber
    [temperature-logger-B_Cu.gbl, temperature-logger-B_Mask.gbs, temperature-logger-B_Paste.gbp, temperature-logger-B_Silkscreen.gbo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]
2022-03-03 all channels will be reported, LEDs now show connection status
2022-03-07 fixed led bug
